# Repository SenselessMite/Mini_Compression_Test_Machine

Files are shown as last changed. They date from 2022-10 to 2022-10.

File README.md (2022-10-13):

# Mini_Compression_Test_Machine
Implementation of a Compression test machine based on Teensy 3.1.
The machine is a University project. It is a prototype of a simple and affordable Traction-Compression
machine made using Open HW and Open Sw, so everyone can make their own.

To assemble it you need the following parts:

For the main circuit:
- teensy 3.1-3.2 for main logic
- 1 linear potentiometer 10kOhm
- SparkFun load cell amplifier HX711 to drive the load cell
- 1 load cell (Model DYLY-103)
- pololu DRV8825 to drive the motor (with heatsink)
- 1 stepper motor (Model 39BYGL215A)
- 1 push button
- 1 two position switch
- 2 1kOhm resistors (pull up for the switch and the push button)
- 2 leds and 2 resistors (the resistance value changes for the led)
- 1 100µF 16v capacitor (for the motor driver)
- 1 7805 voltage regulator (with heatsink)
- 1 1µF capacitor (to stabilize the output of the voltage regulator)
- 1 10µF capacitor (to stabilize the input of the voltage regulator)
- (optional) two position switch to turn on and off the machine
- 12v 2A power source
- jumper

For the wifi module (optional not needed)
- Esp32 wrover module
- Regolatore di Tensione AMS1117 5V
- Lcd display 16 x 2
- 2 10kohm trimmer
- jumper

For the  frame:
- 3d printed parts
- 2 M8 rods (20cm)
- 4 M8 nuts (20cm)
- 6 M8 washers
- 2 8mm rectify rods
- 1 M8 screw (30mm)
- 1 M8 screw (10-15mm)
- 4 M3 screw (15mm)
- 3 M4 screw (30mm)
- 2 M4 nuts

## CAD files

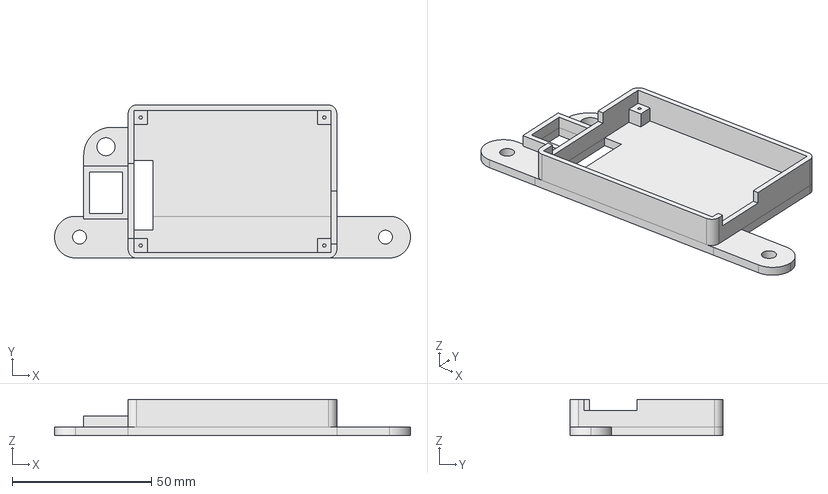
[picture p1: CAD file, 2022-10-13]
FreeCad Files/TCM2 - Main Circuit Box.FCStd
128.0 x 55.0 x 13.0 mm

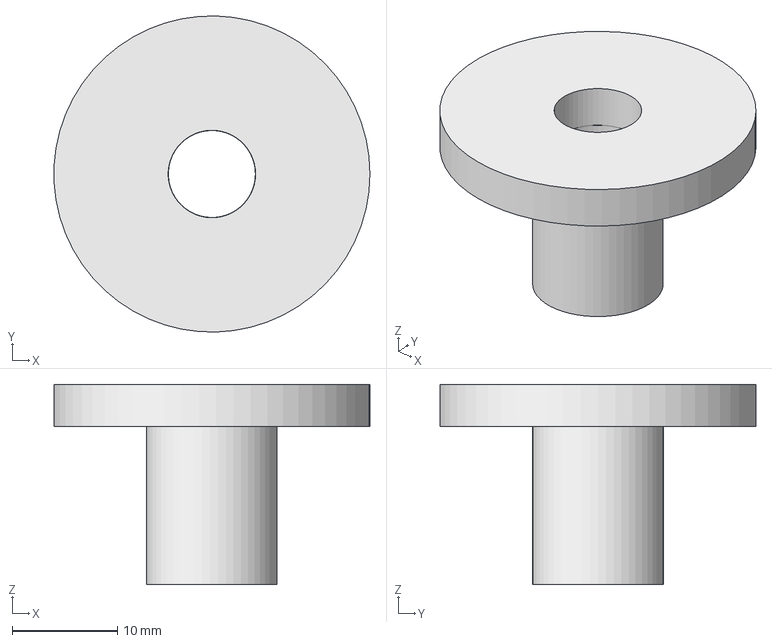
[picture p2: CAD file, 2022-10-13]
FreeCad Files/TCM2 - Adapter M12 - M8.FCStd
30.0 x 30.0 x 19.0 mm

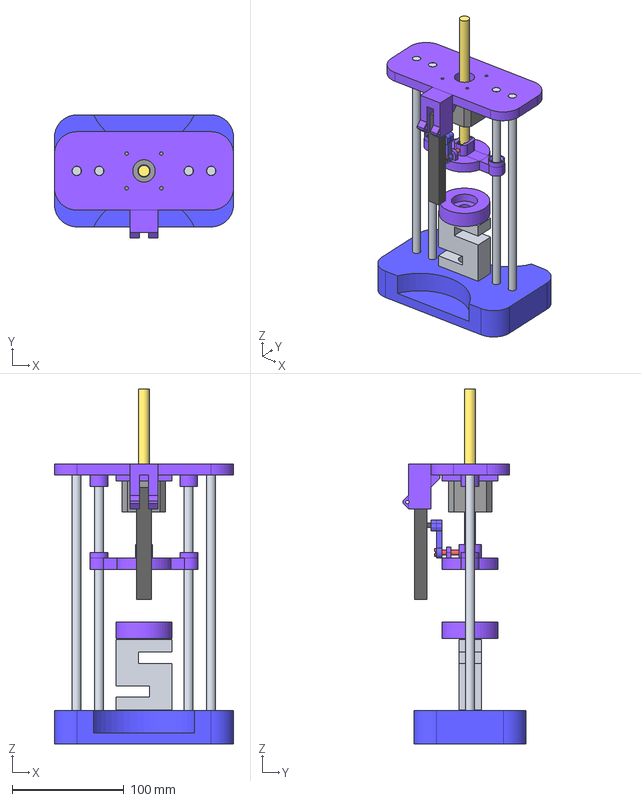
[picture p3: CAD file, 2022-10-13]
FreeCad Files/TCM2 - Build.FCStd
160.0 x 110.0 x 317.0 mm

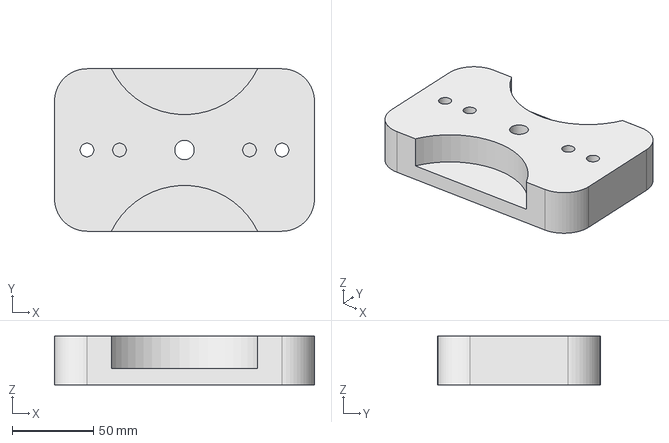
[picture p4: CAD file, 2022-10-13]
FreeCad Files/TCM2 - Base.FCStd
160.0 x 100.0 x 30.0 mm

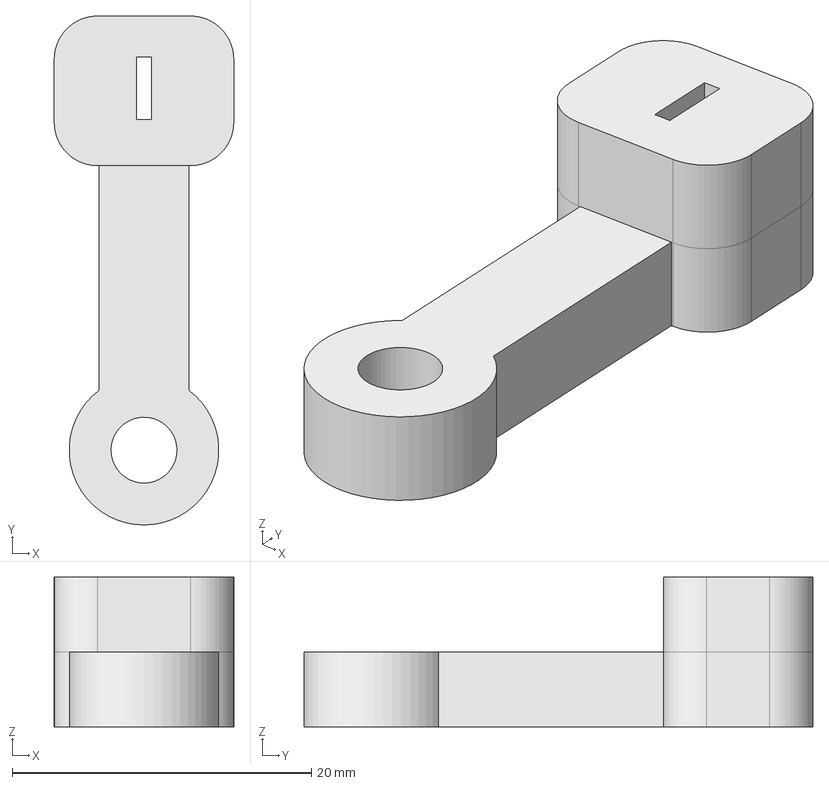
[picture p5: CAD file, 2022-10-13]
FreeCad Files/TCM2 - Column Press Link.FCStd
12.0 x 34.0 x 10.0 mm

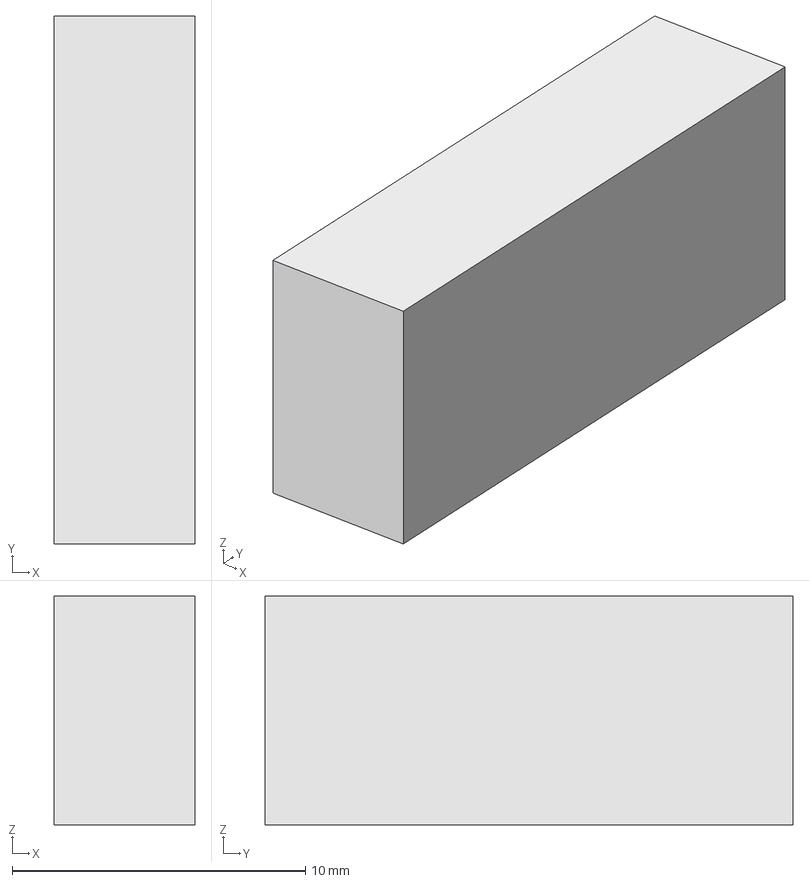
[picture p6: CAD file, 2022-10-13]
FreeCad Files/TCM2 - WiFI Module 3.FCStd
4.80 x 18.0 x 7.80 mm

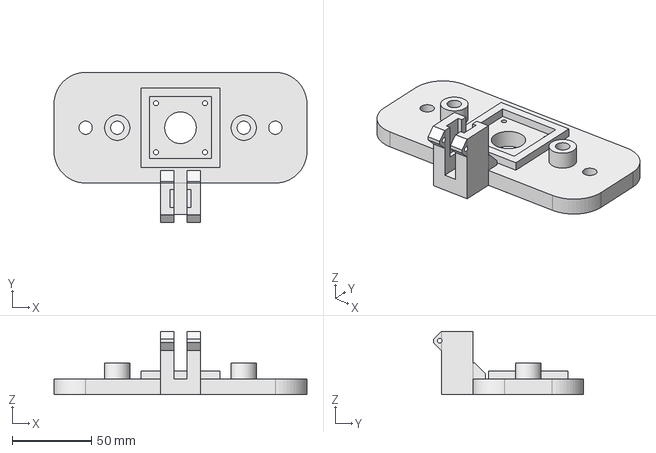
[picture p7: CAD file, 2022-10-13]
FreeCad Files/TCM2 - Top.FCStd
160.0 x 95.0 x 40.0 mm

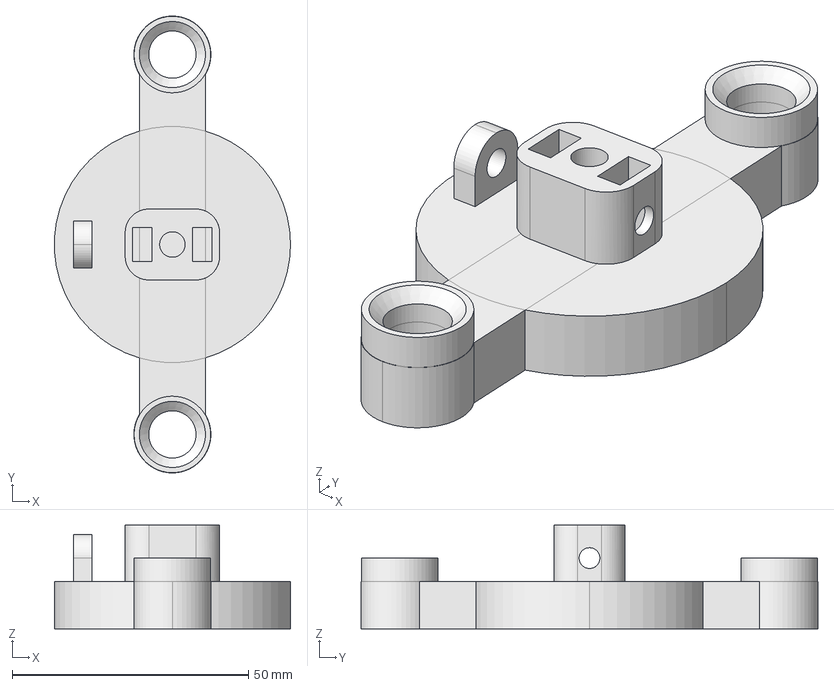
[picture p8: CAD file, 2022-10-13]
FreeCad Files/TCM2 - Column Press.FCStd
50.0 x 96.7 x 22.0 mm

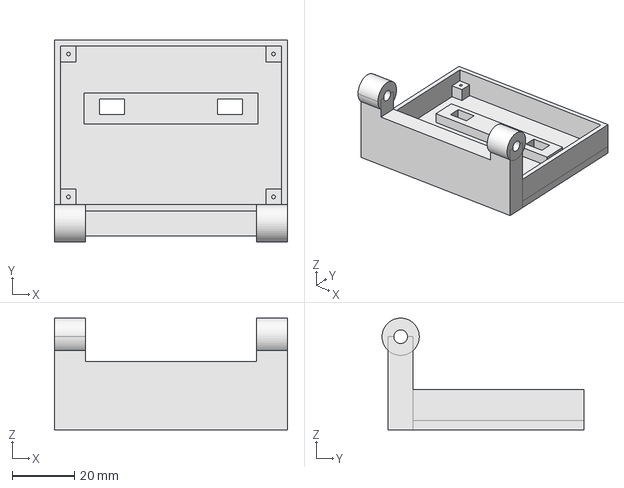
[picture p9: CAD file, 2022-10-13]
FreeCad Files/TCM2 - WiFi Module 1.FCStd
75.0 x 65.0 x 36.0 mm

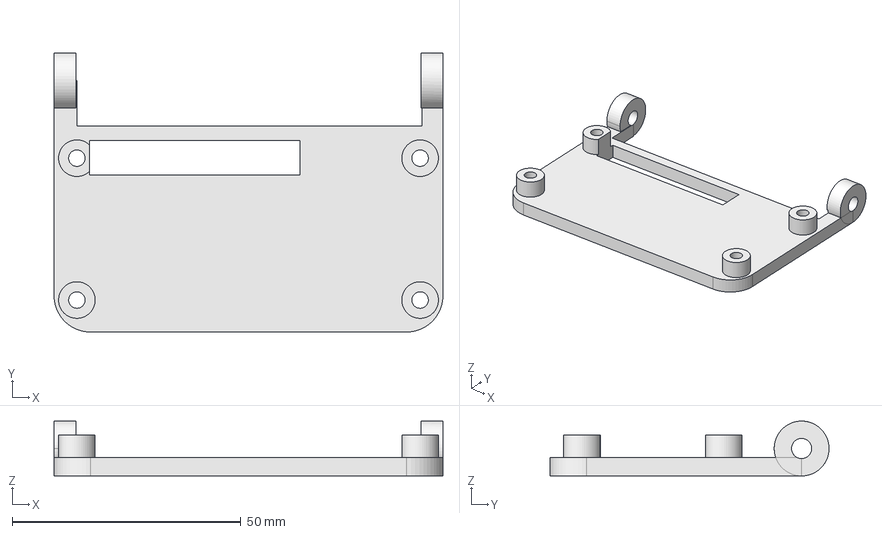
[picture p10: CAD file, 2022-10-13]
FreeCad Files/TCM2 - WiFi Module 2.FCStd
85.0 x 61.0 x 12.0 mm

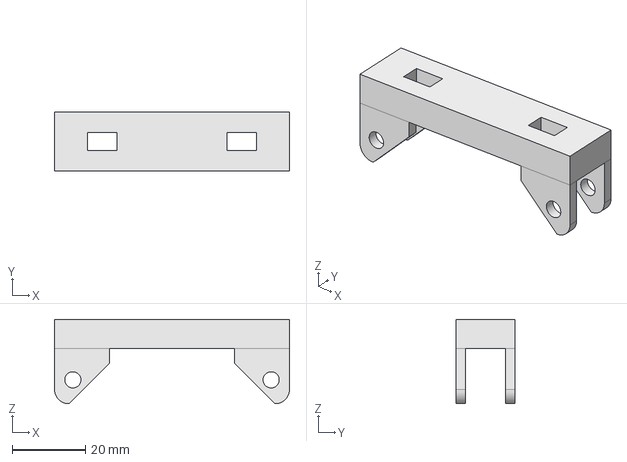
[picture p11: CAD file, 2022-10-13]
FreeCad Files/TCM2 - WiFi Module 4.FCStd
64.0 x 16.0 x 23.0 mm

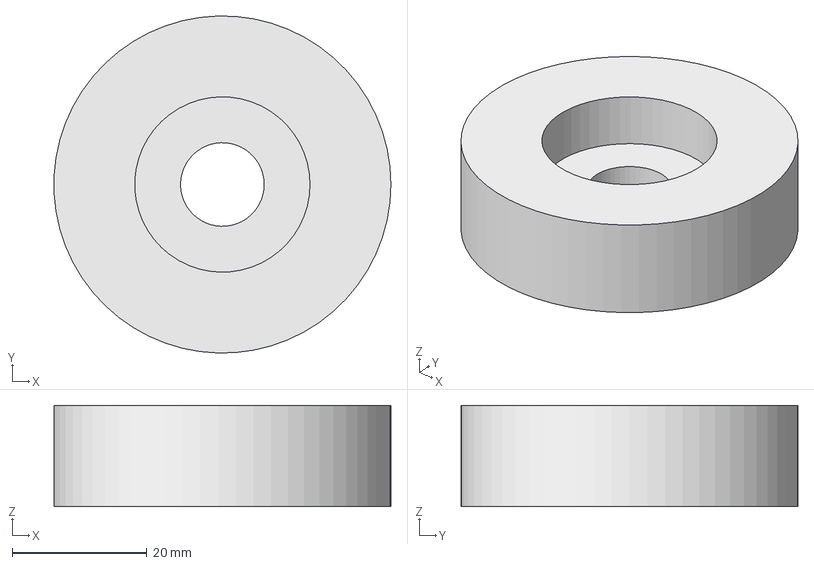
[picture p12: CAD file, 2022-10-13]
FreeCad Files/TCM2 - Load Cell Plate.FCStd
50.0 x 50.0 x 15.0 mm

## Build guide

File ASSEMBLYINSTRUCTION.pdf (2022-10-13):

INSTRUCTION (ITALIANO-ENGLISH)
(BOTTOM):
1) Inserire due Dadi M8 negli appositi fori nella parte inferiore della base del frame Insert two M8 Nuts into the appropriate holes in the lower part of the frame base

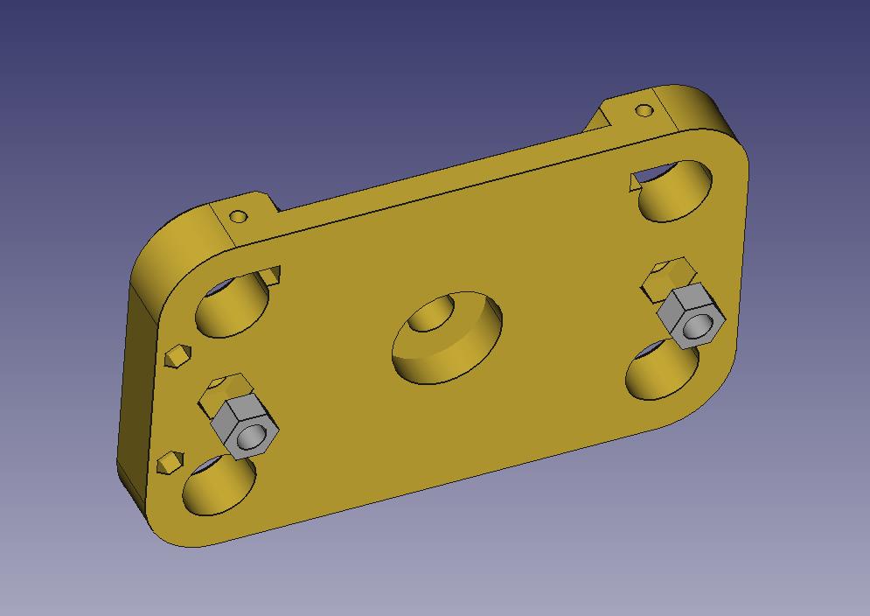
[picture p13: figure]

2) Inserire l’adattatore M12 -M8 all’interno della base del frame dalla parte superiore Insert the M12 - M8 adapter inside the base of the frame from the top

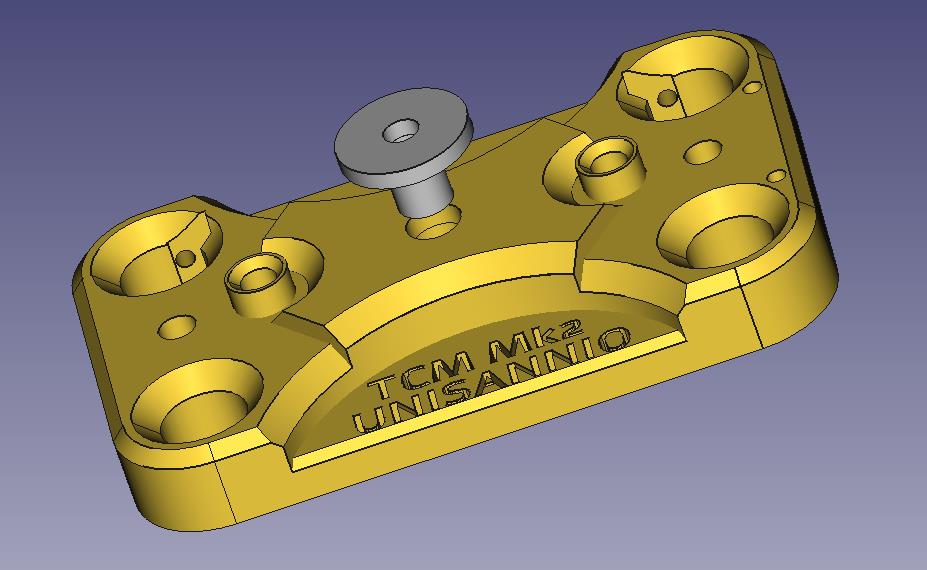
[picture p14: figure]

In

3) Avvita nella base le due barre filettate M8. Screw the two M8 threaded rods into the base.

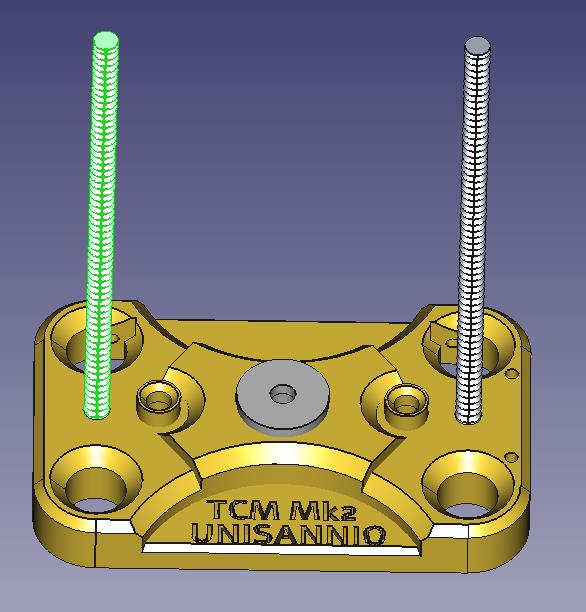
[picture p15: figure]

4) Fissare le due barre filettate M8 alla base con due dadi M8 e due rondelle. Secure the two M8 threaded rods to the base with two M8 nuts and two washers.

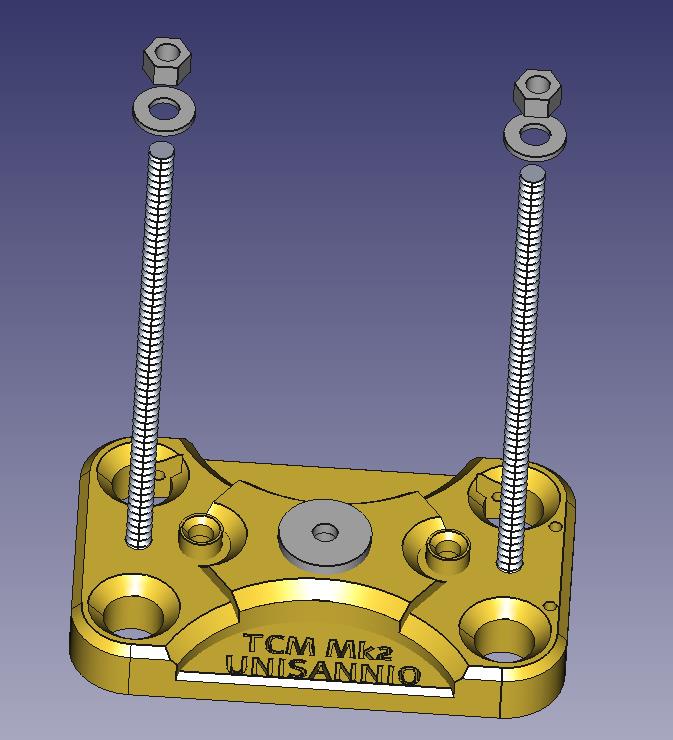
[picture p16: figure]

5) avvita sulle barre filettate M8 due dadi M8 e inserisci due rondelle(una per ogni barra). Avvitale intorno alla metà della barra, serviranno per poter fissare la parte superiore del telaio.
Screw the two nuts on the M8 bars and put two washers on top. This will support the top part of the frame.

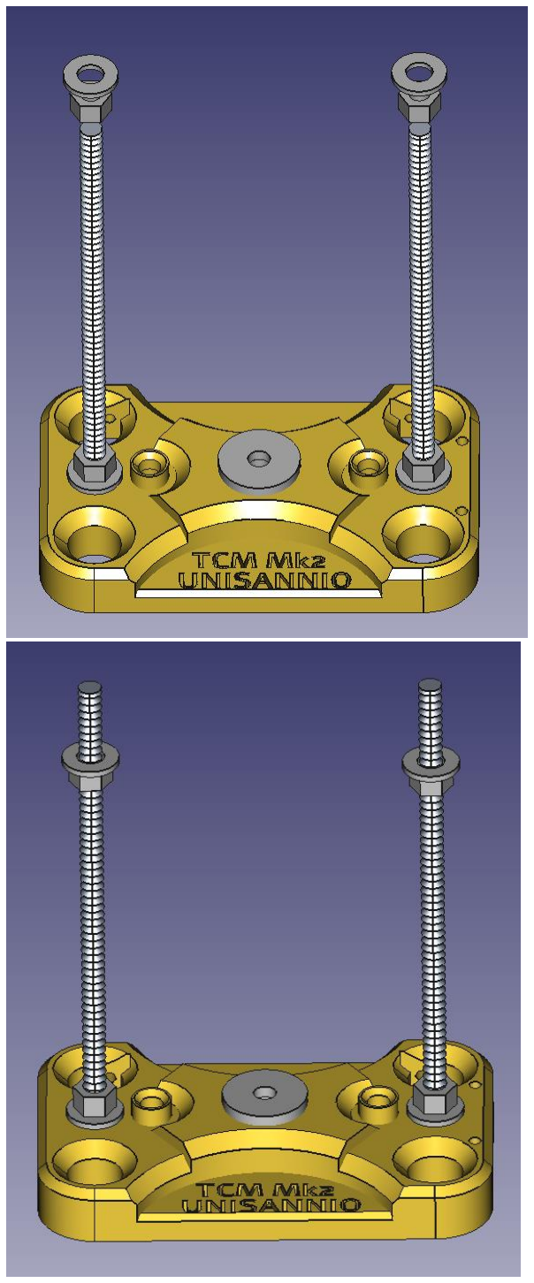
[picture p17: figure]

6) Inserisci nella base le due barre da 8mm rettificate. Insert the two rectified 8mm bars inside the base.

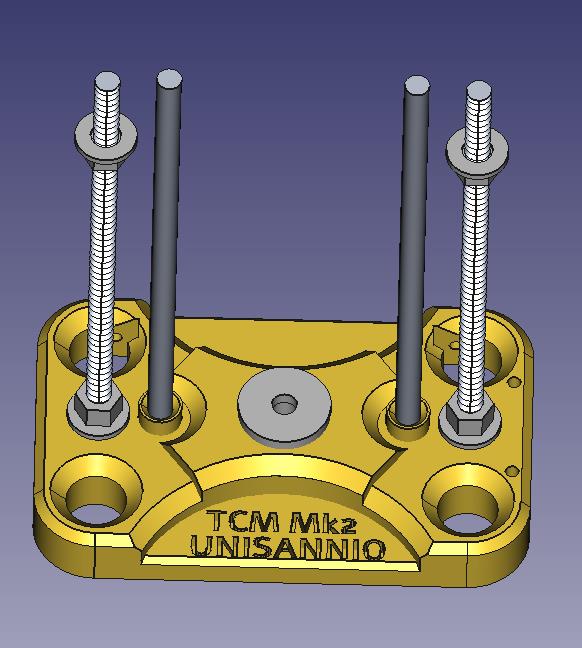
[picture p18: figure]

7) Fissa la cella di carico (seguendo il verso indicato sulla cella stessa) alla base del frame con 1 perno M8 da 30mm, 1 perno M8 da 15mm e due rondelle.
Mount the load cell to the bottom frame with one 30mm M8 bolt and put a 15mm M8 bolt on top the load cell.

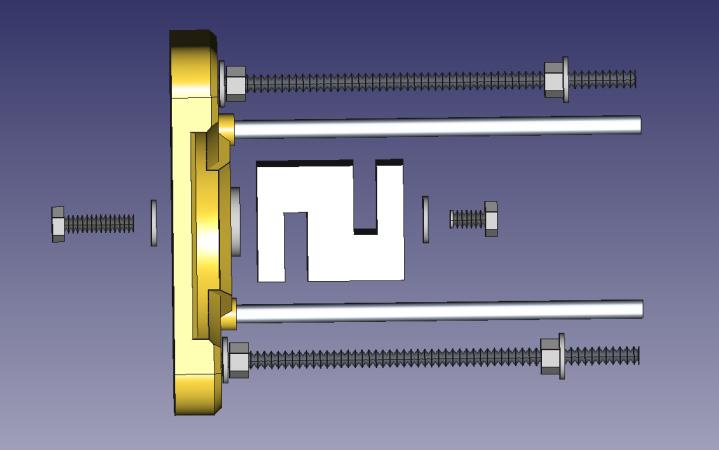
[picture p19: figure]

8) Posiziona il piatto della cella di carico inserendolo sulla testa del perno posto in cima alla cella.
Mount the bottom plate on top of the bolt screwed up on to the load cell.

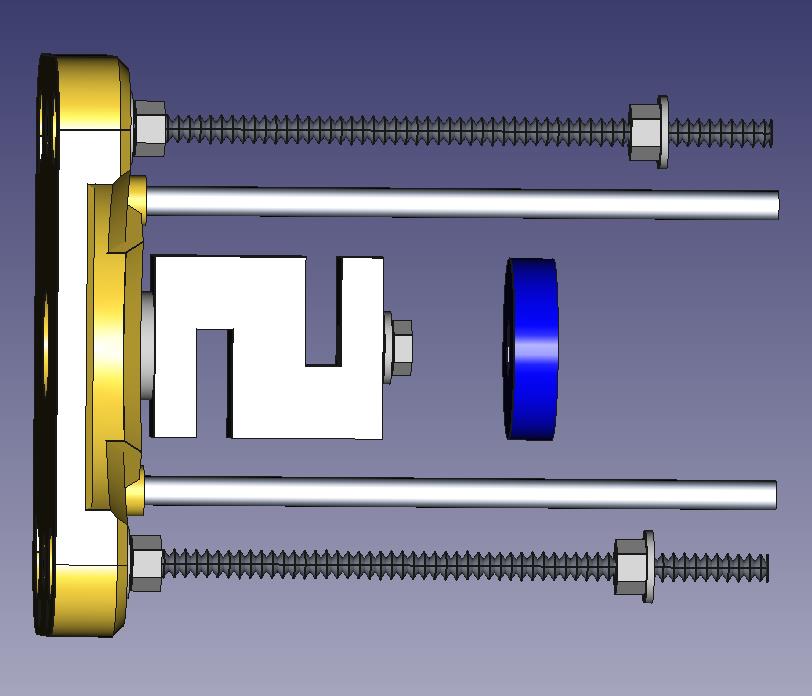
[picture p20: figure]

9) La parte inferiore della macchina è ora completa. The bottom part of the machine is now finished.

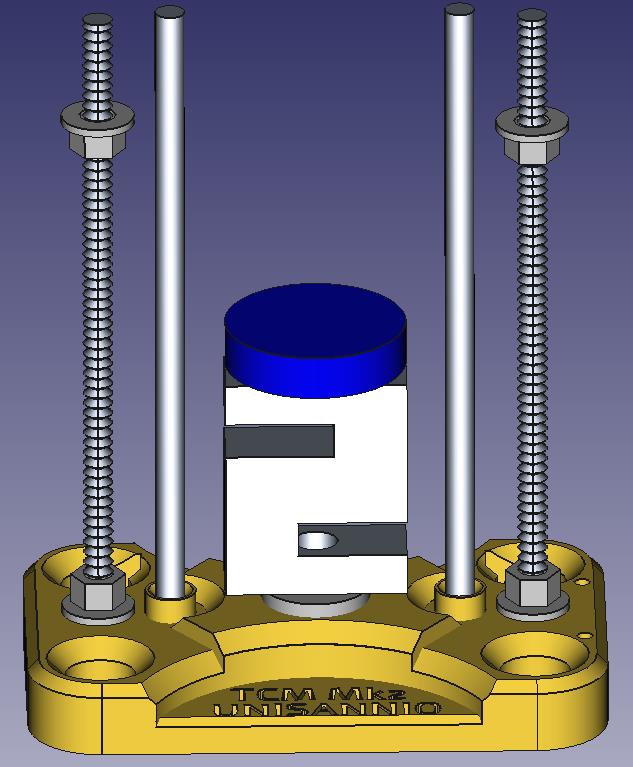
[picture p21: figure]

(TOP):
1) Fissa il motore alla parte superiore del frame con 4 perni M3 da 15mm. Mount the motor to the top frame using 4 M3 bolts 15mm long.

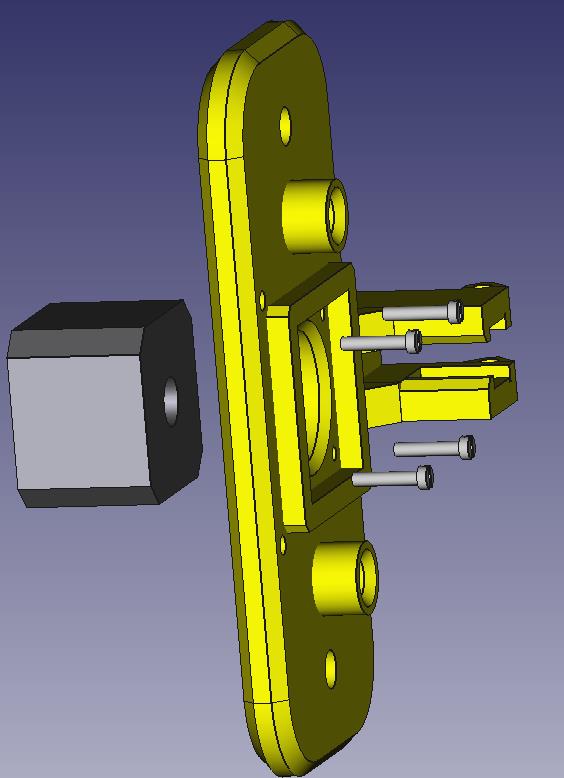
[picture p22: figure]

2) Inserisci l’asse del motore Insert the motor shaft.

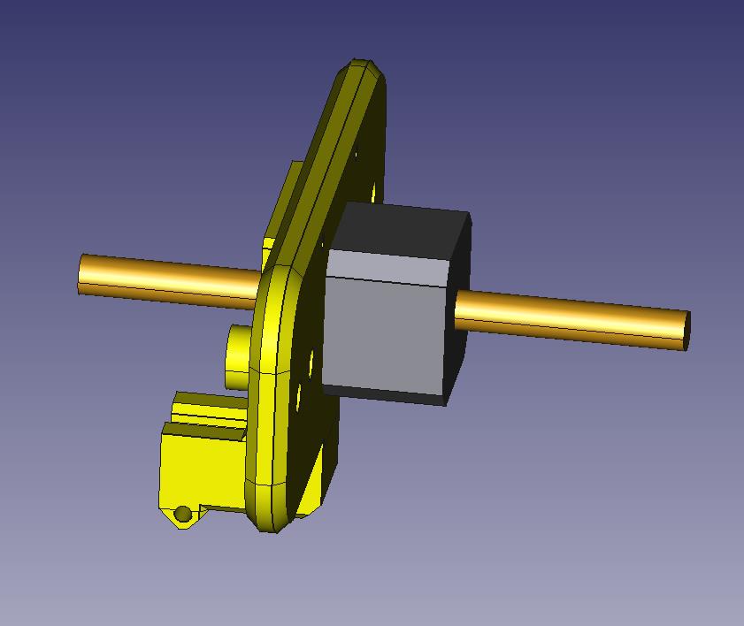
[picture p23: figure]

3) Inserisci due dadi M4 nella pressa
Add two M4 nuts inside the press in the apposit hole.

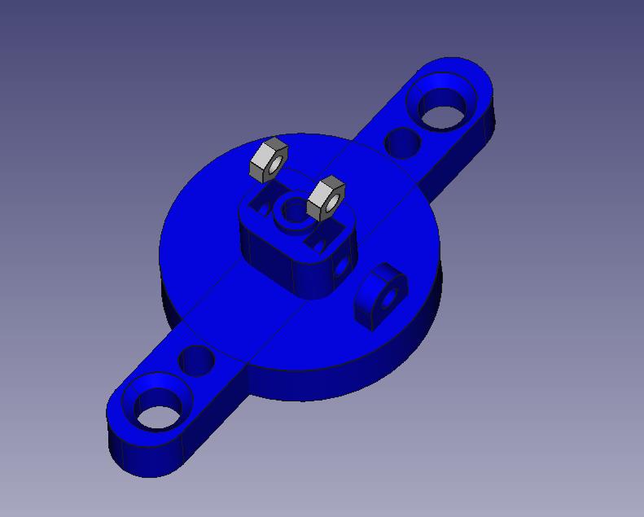
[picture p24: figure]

4) Inserisci il link per il potenziometro con una vite M4 da 30mm e un dado M4 come in figura e inserisci un perno M4 da 15mm dal lato opposto. Non stringere le due viti poichè serviranno per fissare la pressa all’asse del motore.
Mount the link for the potentiometer with a 30mm M4 screw and a M4 nut like in the picture. Insert a 15mm M4 screw in the opposite hole. Don’t tighten the screw because they will be used to fix the press to the motor shaft.

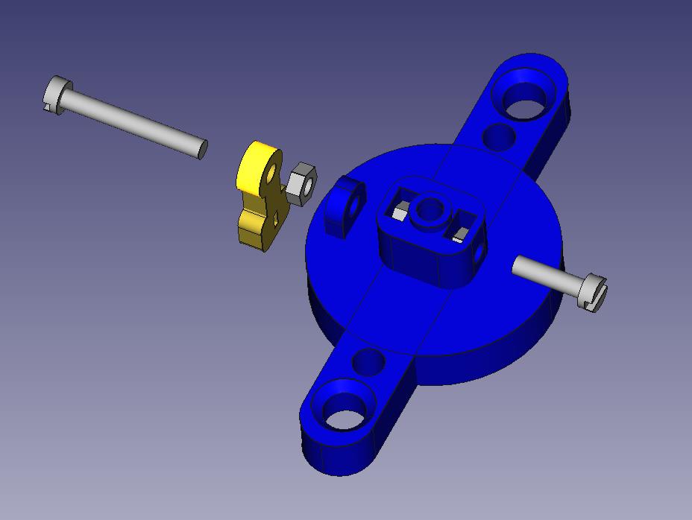
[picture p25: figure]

5) Fissa la pressa al motore con le due viti inserite prima. Mount the press to the motor shaft.

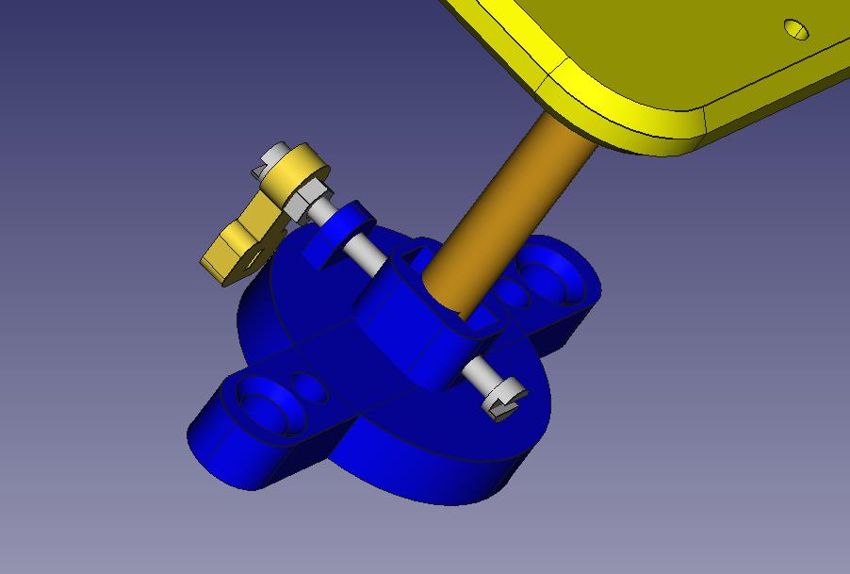
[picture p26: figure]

6) inserisci lo slider del potenziometro nel link fissato alla pressa. Insert the potentiometer in to the hole on the press link.

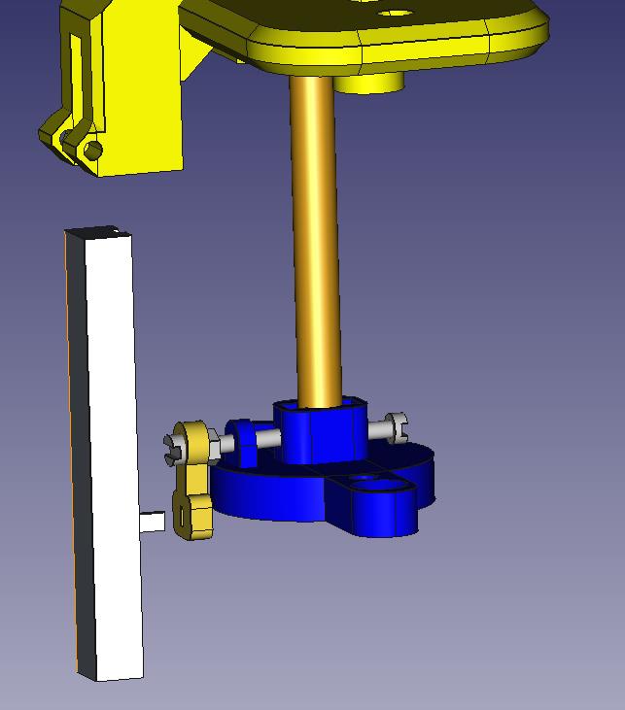
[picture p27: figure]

7) Inserisci il potenziometro nell’apposito slot.
Insert the potentiometer in to the apposite slot of the to frame.

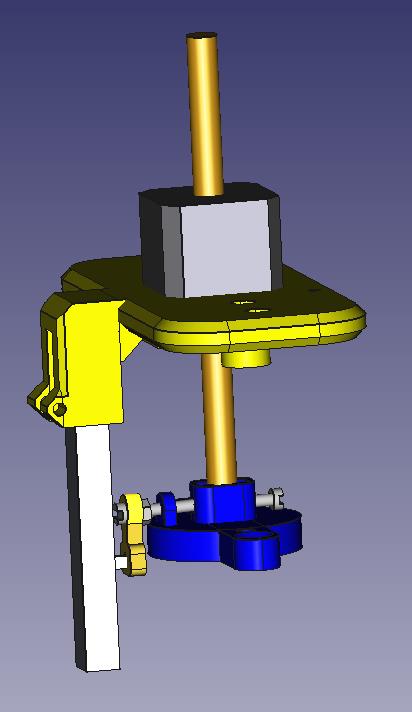
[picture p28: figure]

8) Fissa il potenziometro con una vite M4 da 30mm e un dado M4.
Secure the potentiometer to the top frame with a 30mm M4 bolt and nut.

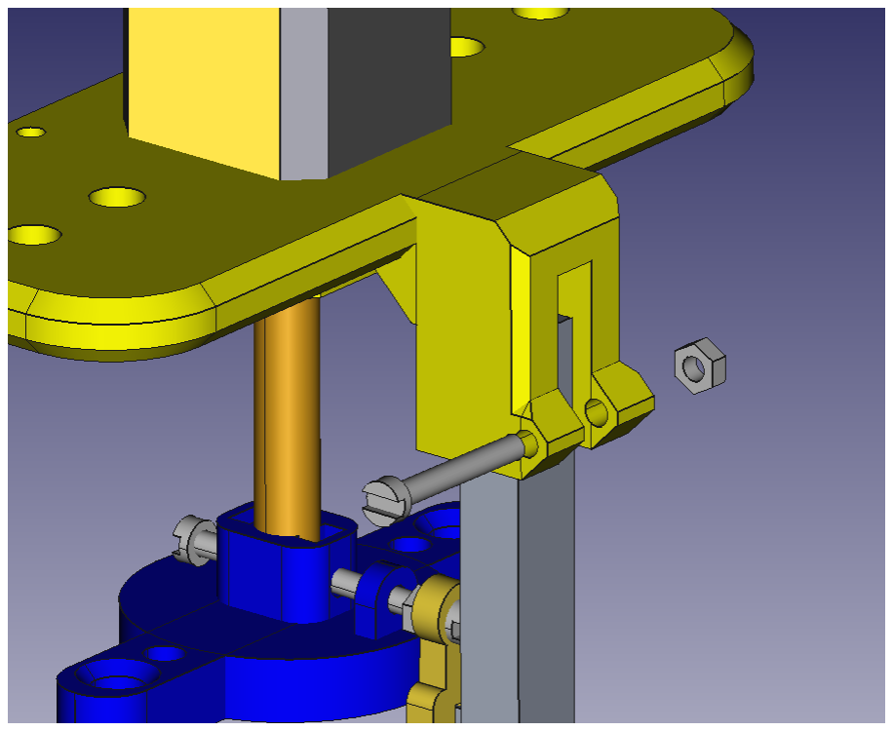
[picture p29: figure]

9) Con questo la parte superiore della macchina è pronta The top part of the machine is now completed.

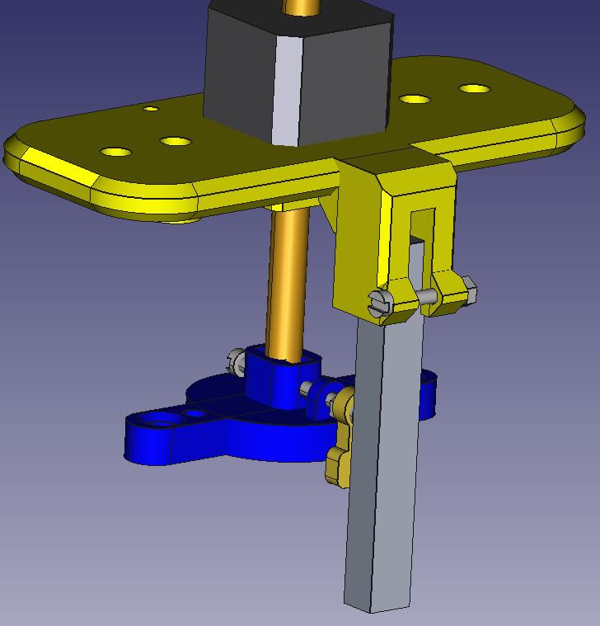
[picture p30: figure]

Passi Finali:
1) Inserisci la parte superiore della macchina sulla parte inferiore (facendo combaciare i fori per le barre filettate M8 e le barre rettificate da 8mm. Utilizza 2 dadi M8 e due rondelle per fissare la parte superiore a quella inferiore insieme ai due dadi e rondelle inseriti al passo (5) delle istruzioni per assemblare la parte inferiore. Per regolare l’altezza aiutarsi con un righello o una squadra.
Insert the top assembly on the bottom assembly. Secure the top part to the bottom part using 2 M8 nuts with washers and a ruler to set the height of the top part.

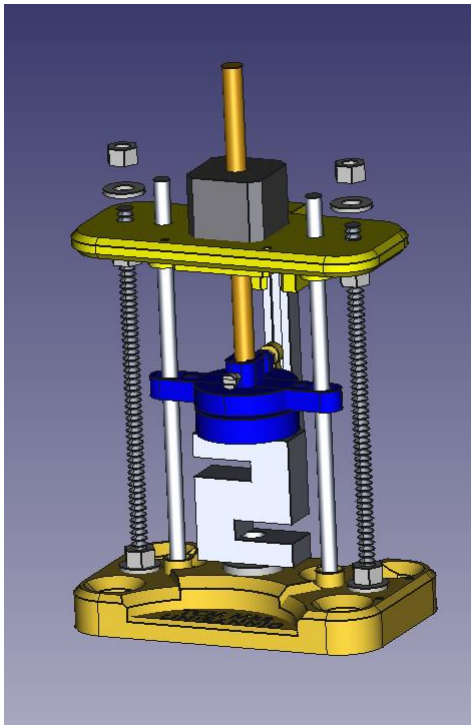
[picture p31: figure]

2) Finito! Il frame della macchina è pronto Now the machine is completed.

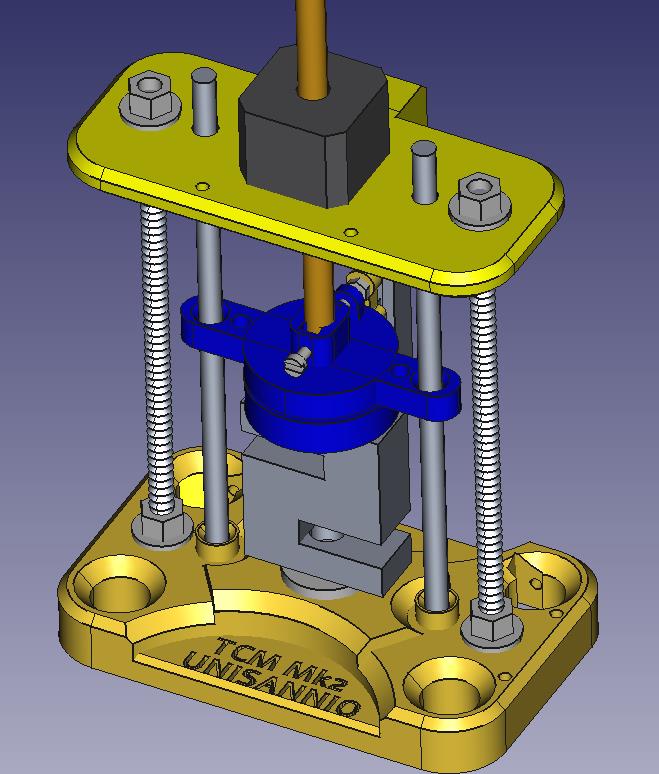
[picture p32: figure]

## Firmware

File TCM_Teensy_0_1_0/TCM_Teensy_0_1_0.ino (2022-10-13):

/*
 * T-C Machine:
 *    This is a OPEN HARDWARE and OPEN SOFTWARE prototype for a Traction compression machine
 *    This driver is designed to work on a Teensy 3.1/3.2 board
 */

/*
 * Library included:
 *    - parameters.h contains all the constant parameters for the machine
 *    - pinout.h contains the definition of the pin used
 *    - ADC.h it is used for analog-digital conversion of the potentiometer value
 *    - TeensyStep.h is used to drive the stepper motor
 *    - IntervalTimer.h is the librar
 *    - HX711.h is the library for the SparkFun HX711 Load Cell Amplifier
 */
#include "parameters.h"
#include "pinout.h"

#include <ADC.h>
#include <TeensyStep.h>
#include <IntervalTimer.h>
#include <HX711.h>

ADC *adc = new ADC(); //ADC obbject 

IntervalTimer timer0; //Timer Object

HX711 scale;//Load Cell Object

/*
 * The variable mod is used to mantain the operational status of the machine:
 *    - if mod = false the machine is used in serial monitor mode and selSerial is set to Serial
 *    - if mod = true the machine is used in web mode and selSerial is set to Serial1
 */
boolean mod = false;

Stream *selSerial;//serial communication currently selected
/*
 * LMIN and LMAX are used to save the min and max position for the potentiometer
 *    - LMIN is position 0;
 *    - LMAX is the position when the column touch the load cell plate
 *    
 * The two variables are set in the autoCalibration function
 */
float LMIN=0; //minimum position potentiometer
float LMAX=0; //maximum position potentiometer

/*
 * Status variable for the machine:
 *    - ES is the displacement set for the measurement
 *    - SPEED is the speed of the motor expressed in mm/min
 *    - TS is the sampling time for the measure
 *    - NC is the number of measuring cycles 
 */
float ES= DEF_ES;   // displacement [mm]
float SPEED=DEF_SPEED;// spedd [mm/min] 
int TS=DEF_TS;   // sampling time [ms]
int NC=DEF_NC;     // number of cycles

float ES0=ES;  //displacement zero


/*
 * The following variables are used to set the machine 
 * parameters and are automatically obtained from the variables: ES, SPEED, TS, NC
 *    - VSTP indicates the speed of the motor in stp/s
 *    - POS indicates the number of steps for the current displacement
 *    - POSI is an integer approximation  of POS
 *    - TTOT indicates the time required to carry out the measurement process
 *    - NP indicates the number of measurements to be made
 *    - MAX_NC indicates the max number of cycles
 */
//int RPMSP=(int)(SPEED/PAS/MOTOR_STEPS*F1); // [rotation/min] motor speed in rpm 
int VSTP=(int)(SPEED/PAS/60*F1*MCRSTP); // [stp/s] motor speed in step
float POS=ES/PAS*MCRSTP; // total steps for the current displacement
int POSI=(int)POS; // approximation of POS
float TTOT=(2*NC*ES/SPEED*60); // [s] Total measurement time
//const int TP=(int)(1000*TTOT/POS); // [ms] single step time 
int NP=(int)(TTOT*1000/TS); // total number of measurement point
int MAX_NC = 0; // max cycle number for the current setting



/*
 * Array used to save the results of the measurement process
 *    - vTime contains the value of the time for the current measure
 *    - vPosition contains the value of the displacement for the current measure
 *    - vLoad contains the value read from the load cell for the current measure
 */
long vTime[NN];
int  vPosition[NN];
float vLoad[NN];

/*
 * variables used to measure time 
 */
unsigned long time1, time0, wait_time;

/*
 * Global variables used for generic operation
 */
int x=0; // loop index
long P0=0; // initial position for the potentiometer
float limo=1; // variable used to set the distance that the motor must travel
char r0; // command received

/*
 * This variable is used to stop the execution of the machine if the use mode is changed
 */
boolean endOperation;
boolean abortop = false;

/*
 * Indicate if there is a measure already saved
 */
boolean savedMeasure = false;

/*
 * Object used to define the motor and to control it:
 *    - motor is a basic 2-wires configuratio for the motor
 *    - controller is the object that operate the driver for the motor
 */
Stepper motor(STEP, DIR);   
StepControl controller;    // Use default settings 

/*
 * SETUP
 */
void setup() {
  
     //Set default motor speed and acceleration
     motor.setMaxSpeed(VSTP);         // stp/s
     motor.setAcceleration(VSTP*3);    // stp/s^2
     
     //Set DRV8825 pin
     pinMode(ENBL, INPUT);
     pinMode(RES, OUTPUT);
     pinMode(SLP, OUTPUT);

     disable();// disable the motor
     
     pinMode(MODE0, OUTPUT);
     pinMode(MODE1, OUTPUT);
     pinMode(MODE2, OUTPUT);
     
     //Set microstep level
     digitalWrite(MODE0, MOD0V);
     digitalWrite(MODE1, MOD1V);
     digitalWrite(MODE2, MOD2V);
     
     pinMode(LED0, OUTPUT);
     pinMode(LED1, OUTPUT);
     pinMode(ABRT, INPUT);
     
     pinMode(MODS, INPUT);
     pinMode(SESP, OUTPUT);
     
     attachInterrupt(digitalPinToInterrupt(ABRT), abortOP, CHANGE);
     //attachInterrupt(digitalPinToInterrupt(ESPABORT), abortOP, CHANGE);
     
     
     
     scale.begin(P_DOUT, P_SCK);
     scale.set_scale(HX_SC);     // this value is obtained by calibrating the scale with known weights; see the README for details
     scale.tare();      // reset the tare to 0
    
     // ADC resolution - 12bit: 0-4095, 13bit: 0-8191
     adc->adc0->setAveraging(16); // set number of averages
     adc->adc0->setResolution(12); // set bits of resolution
     adc->adc0->setReference(ADC_REFERENCE::REF_3V3);

     // it can be any of the ADC_CONVERSION_SPEED enum: VERY_LOW_SPEED, LOW_SPEED, MED_SPEED, HIGH_SPEED_16BITS, HIGH_SPEED or VERY_HIGH_SPEED
     // see the documentation for more information
     // additionally the conversion speed can also be ADACK_2_4, ADACK_4_0, ADACK_5_2 and ADACK_6_2,
     // where the numbers are the frequency of the ADC clock in MHz and are independent on the bus speed.
     adc->adc0->setConversionSpeed(ADC_CONVERSION_SPEED::MED_SPEED); // change the conversion speed
     // it can be any of the ADC_MED_SPEED enum: VERY_LOW_SPEED, LOW_SPEED, MED_SPEED, HIGH_SPEED or VERY_HIGH_SPEED
     adc->adc0->setSamplingSpeed(ADC_SAMPLING_SPEED::MED_SPEED); // change the sampling speed
    
     //Serial1 is used for the communication with the ESP32
     Serial1.begin(115200);
     digitalWrite(SESP, LOW);
     Serial1.print("INIT");
     autoCalibration();
     delay(2000);
     Serial.begin(115200);

     //Set the use mode for the machine
     if(digitalRead(MODS) == HIGH){
        mod = true;
        selSerial = &Serial1;
        digitalWrite(SESP, HIGH);
        clearSerial();
     }else{
        mod = false;
        selSerial = &Serial;
        digitalWrite(SESP, LOW);
        clearSerial();
     }
     MAX_NC = maxNC(NC, SPEED, ES, TS);
     Serial.println(MAX_NC);
     //pinMode(ESINT, OUTPUT);
     //digitalWrite(ESINT, LOW);
     // Set the DATE and TIME 
     //flash_data("$TIME 09:00:00"); 
     //flash_data("$DATE 2018-01-01"); 
     //pinMode(ESPABORT, INPUT);
}

//------------------------------MAIN------------------------------
void loop() {
   switchMode();//switch use mode
   Serial.println("Traction Compression machine\n");
   endOperation=false;
   while(!endOperation){
      digitalWrite(LED0, HIGH);
      digitalWrite(LED1, LOW);

      //Print the Serial menu, only for serial monitor mode
      printMenu();

      //read the commad and and check if there has been a change of use mode
      r0 = serialSwitchOnCommand();

      switch (r0){
        /*
         * b command set the default parameter for SPEED, ES, TS, NC.
         * The default value are setted in the parameters.h
         */
        case 'b':
        case 'B':
          setDefaultParameters();
          break;
        /*
         * Command used to debugging purpose
         */
        case 'l':
        case 'L':
          sendMeasure();
          break;
        /*
         * u command move the column towards the load cell. 
         * When the load read from the cell is greater then 0.2 the column stops 
         */
        case 'u':
        case 'U':
          moveToSample();
          break;
        /*
         * j command start the autocalibration procedure
         */
        case 'j':
        case 'J':
          autoCalibration();
          break;
        /*
         * g command write the status of the machine on the selSerial
         */
        case 'g':
        case 'G':
          sendStatus();
          break;
        /*
         * h command return the column to the 0 position of the potentiometer
         */
        case 'h':
        case 'H':
          returnHome();
          break;
        /*
         * d command read the value for the displacement from the 
         */
        case 'D':
        case 'd':
          Serial.println("d command, insert displacement [mm]: ");
          Serial.println("Please, be sure that plates do not touch! ");
          setDisplacement();
          //TODO aggiungere invio errore ne caso di problema con i valori inseriti per il displacement
          break;
        case 'S':
        case 's':
          Serial.println("s command, insert speed [mm/min]: ");
          setMSpeed();
          break;
        case 'T':
        case 't':
          Serial.println("t command, insert sampling time [ms]: ");
          Serial.println(" 150ms<sampling time<1000ms ");
          setSamplingTime();
          break;
        case 'N':
        case 'n':
          Serial.println("n command, insert number of cycles: ");
          setNumberOfCycles();
          break;
        case 'C':
        case 'c':
          Serial.print("c command, move the column, insert (mm) (<0 go down): ");
          moveColumn();
          break;
        case 'A':
        case 'a':
          Serial.println("a command, reset actual tare to 0 ");
          scale.tare();      // reset the tare to 0
          break;
        case 'M':
        case 'm':
          Serial.println("Hai digitato il comando m. Effettua la misura ");
          startMeasure();
          break;
      default:
        Serial.println("Invalid command");
        delay(100);
     }
     abortop = false;      
   }
   delay(1000);
   Serial.println("Changing the use mode");    
}// END main loop-----------------------------

//--------------------FUNCTIONS----------------


/*
 * Print the menu for the serial monitor mode
 */
void printMenu(){
    Serial.println("________________________________________________");
    Serial.print("Initial load: ");
    Serial.print(scale.get_units(5));
    pos0(); // misura posizione iniziale P0
    Serial.print("N; pos: ");
    Serial.print(P0*SCE);
    Serial.print("mm; Stp/s: ");
    Serial.print(VSTP);
    Serial.print("; Tot time: ");
    Serial.print(TTOT);
    Serial.print("s; Tot steps: ");
    Serial.print(POSI, 1);
    Serial.print("; Meas. points: ");
    Serial.println(NP, 1);
    Serial.println("________________________________________________");
    Serial.println(" Select a command: ");
    Serial.print(" d - relative displacement [mm], (");
    Serial.print(ES);Serial.println("): ");
    Serial.print(" s - speed [mm/min], (");
    Serial.print(SPEED);Serial.println("): ");
    Serial.print(" t - sampling time [ms], (");
    Serial.print(TS);Serial.println("): ");
    Serial.print(" n - number of cycles, (");
    Serial.print(NC);Serial.println("): ");
    Serial.println(' ');
    Serial.println(" c - MOVE THE COLUMN [mm]");
    Serial.println(" h - MOVE THE COLUMN TO HOME POSITION");
    Serial.println(" u - MOVE THE COLOUMN TO SAMPLE FOR MEASURE");
    Serial.println(" a - RESET ACTUAL TARE TO ZERO");
    Serial.println(" b - RESET PARAMETERS TO DEFAULT VALUE");
    Serial.println(" m - MEASURE");
    Serial.println("________________________________________________");
    Serial.println(' ');
}//end printMenu-------------------------------
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

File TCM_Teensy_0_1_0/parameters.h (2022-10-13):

/*
 * This file includes setting parameters for the machine
 */

#ifndef PARAMETERS_H
#define PARAMETERS_H

/*
 * Setting parameters for the stepper motor
 */
const int  MOTOR_STEPS=200; // number of steps for a complete rotatio of the motor
const float PAS=0.01; // [mm] move with each step
const int MCRSTP=32; //microstep level selected

/*
 * Variables used to set the microsteplevel for the DRV8825 driver
 *    - MODE0, MODE1 and MODE2 are used to set the micro step level of the driver:
 *        - MODE0 = LOW, MODE1 = LOW, MODE2 = LOW for full step
 *        - MODE0 = HIGH, MODE1 = LOW, MODE2 = LOW for half step
 *        - MODE0 = LOW, MODE1 = HIGH, MODE2 = LOW for 1/4 step
 *        - MODE0 = HIGH, MODE1 = HIGH, MODE2 = LOW for 1/8 step
 *        - MODE0 = LOW, MODE1 = LOW, MODE2 = HIGH for 1/16 step
 *        - MODE0 = HIGH, MODE1 = LOW, MODE2 = HIGH for 1/32 step
 *        - MODE0 = LOW, MODE1 = HIGH, MODE2 = HIGH for 1/32 step
 *        - MODE0 = HIGH, MODE1 = HIGH, MODE2 = HIGH for 1/32 step
 */
const int MOD0V = HIGH;
const int MOD1V = HIGH;
const int MOD2V = HIGH;

/*
 * Setting parameters for the potentiometer
 */
const float VIN=3.3; // power supply voltage of the potentiometer
const float MDE = 55.0; // maximum range of positions recorded by the potentiometer  [mm]
const float SCE=MDE/4095; //potentiometer scale on 12 bits

/*
 * Setting parameters for the load cell
 */
//const float HX_SC=438.48; // scale for the result in grams
const float HX_SC=44713; // scale for the result in Newton (438.48*1000/9.81)

/*
 * User parameters
 */
//const float F1=1.666667;
const float F1=1;

/*
 * Limit Parameters
 *    - MAXTS is the max value for the sampling time
 *    - MINTS is the min value for the sampling time
 *    - MAXSPEED is the max value for the motor speed
 *    - MINSPEED is the min value for the motor speed
 */
const int MAXTS = 1000;
const int MINTS = 100;
const float MAXSPEED = 55.0;
const float MINSPEED = 5.0;

/*
 * Default parameters
 *    - default value for the parameters SPEED, ES, NC, TS and NN
 */
const float DEF_SPEED = 30.0;
const float DEF_ES = 5.0;
const int DEF_NC = 1;
const int DEF_TS = 500;
const int NN=1400; // dimension for the measurement arrays
#endif
